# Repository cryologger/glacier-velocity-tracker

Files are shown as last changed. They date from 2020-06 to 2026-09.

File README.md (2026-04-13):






# Cryologger - Glacier Velocity Tracker (GVT)
### Note: This documentation is currently under development.
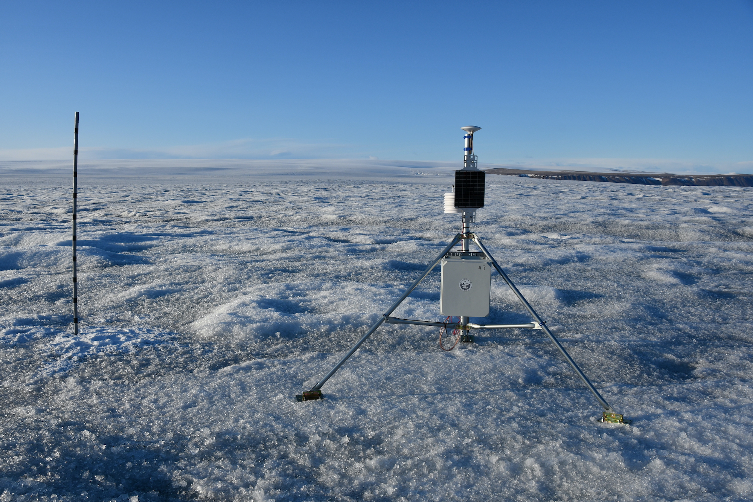
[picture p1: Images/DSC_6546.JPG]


## 1.0 Introduction

Reliance on expensive and proprietary commercial data acquisition and telemetry systems can present a barrier to monitoring remote polar environments. The development of low-cost, open-source instrumentation can greatly reduce the cost of research in remote locations, improve the spatiotemporal resolution of collected data, and provide new ways to observe and monitor the cryosphere. 

The [Cryologger Glacier Velocity Tracker (GVT)](https://github.com/cryologger/glacier-velocity-tracker) is a novel [Cryologger](https://github.com/cryologger) design configuration intended to collect high temporal resolution velocity measurements to assess glacier dynamics on daily timescales in the Canadian Arctic. The system is based on the Arduino electronics platform and harnesses the u-blox ZED-F9P multi-frequency Global Navigation Satellite System (GNSS) receiver.

## 2.0 Methods

### 2.1 Design
The Cryologger GVT is based on the open-source Arduino platform (www.arduino.cc). Code is written using the Arduino Integrated Development Environment (IDE) and benefits from the availability of community-generated libraries.

The design of the Cryologger GVT takes into consideration several key principles, including cost-effectiveness, power efficiency, modularity, ruggedness, and ease of use. It is comprised of off-the-shelf components that do not require specialized tools or training, making it accessible to researchers, citizen scientists, and hobbyists alike. These selected components are also resistant to harsh environmental conditions, ensuring year-round continuous cold-weather operation.

#### 2.1.1 Bill of materials

The Cryologger GVT is built using almost exclusively using components from [SparkFun](https://www.sparkfun.com/), with a list of the main components shown below. For a more detailed bill of materials, including requirements for power and mounting of a complete deployable system, please see [ASSEMBLY.md](/Documentation/ASSEMBLY.md).

**Table 1.** Main components making up Cryologger GVT. Prices are listed in USD and are current as of December 2023. Taxes and shipping are not included.
| Component | Product | Quantity | Cost (USD) |
| --- | --- | :---: | :---: |
| PCB | [Custom Cryologger Printed Circuit Board](https://jlcpcb.com) | 1 | $5.00 | 
| Processor | [SparkFun MicroMod Artemis Processor](https://www.sparkfun.com/products/16401) | 1 | $14.95 | 
| Carrier Board | [SparkFun MicroMod Data Logging Carrier Board](https://www.sparkfun.com/products/16829) | 1 | $21.50 | 
| GNSS Receiver | [SparkFun GPS-RTK-SMA Breakout - ZED-F9P](https://www.sparkfun.com/products/16481) | 1 | $274.95 | 
| GNSS Antenna | [SparkFun GNSS Multi-Band L1/L2 Surveying Antenna (TNC) - TOP106](https://www.sparkfun.com/products/17751) | 1 | $133.95 | 
| Display | [SparkFun Qwiic OLED Display](https://www.sparkfun.com/products/17153) | 1 | $10.95 |
| Voltage Regulator | [Pololu 5V, 600mA Step-Down Voltage Regulator D36V6F5](https://www.pololu.com/product/3792) | 1 | $6.95 |

#### 2.1.2 Design Evolution 

A carrier board was designed to simplify assembly and deployment. It provides 5.08 mm, 2-pin screw terminals for wiring the battery connection, and a resistor divider to measure battery voltage.


<p align="center"><b>Figure 1.</b> Open-source carrier board design.</p>

#### 2.1.3 Mock-up
The Cryologger GVT was originally intended to be installed in a small electronics enclosure that is mounted in a larger enclosure for deployment outdoors.


<p align="center"><b>Figure 2.</b> Open-source carrier board design.</p>

### 2.2 Operation

When initially powered on, the Cryologger GVT will attempt to establish a GNSS fix and synchronize the real-time clock (RTC) of the MicroMod Artemis Processor for up to 5 minutes. Once the RTC is synchronized, the system will set an alarm to wake at the user-specified time and then enter a low-power deep sleep.  Nominally, the system will wake daily and log data from the u-blox GNSS receiver to a microSD card for a period of 3 hours. There are three different logging modes available to the end end-user, which can be tailored to the data collection requirements and available power capacity.

Versions 2.2.1 and above of the Cryologger GVT are equipped with an OLED display. This display is used to provide detailed information to the end user about the status of the Cryologger at each stage of operation, including boot-up, initialization of components, acquisition of GNSS fix, and logging of data. 

In addition to the OLED display messages, a series of LED blink patterns can also be used to indicate system operation and guide possible troubleshooting steps that should be attempted if any errors is encountered. A detailed table of the LED blink patterns can be found in the [DEPLOYMENT.md](/Documentation/DEPLOYMET.md) documentation. 

While the system is in deep sleep, a Watchdog Timer (WDT) will wake the system to check the program has not frozen every 10 seconds and perform a reset, if necessary. This helps to ensure the long-term reliability of the system.

### 2.3 Data Processing

Data is logged in u-blox's proprietary .ubx format. Log files can be converted to RINEX using RTKLIB or Emlid Studio and submitted to NRCan's Precise Point Positioning (PPP) tool: https://webapp.geod.nrcan.gc.ca/geod/tools-outils/ppp.php

For a more detailed guide on the processing of data, please see "[PROCESSING.md](/Documentation/PROCESSING.md).

## 3.0 Deployments

Between 2021 and 2023, a total of 28 Cryologger GVT deployments were made by several different academic institutions, including the Univerity of Ottawa, Carleton University, University of Waterloo (Canada), Carnegie Mellon University (United States), and University of Fribourg (Switzerland). These deployments were made on glaciers in several geographically distinct locations, including Canada, the United States and Kyrgyzstan. Two case studies of deployments made by the University of Ottawa and the University of Waterloo on glaciers in the Yukon and Nunvaut, Canada are explored in more detail below.


<p align="left"><b>Figure 3.</b> Map of Cryologger GVT deployments made between 2021 and 2023.</p>

### 3.1 Lowell Glacier, Yukon, Canada


<p align="left"><b>Figure 4.</b> Map of Cryologger GVT deployments made in 2021 on the Lowell Glacier, Yukon.</p>

### 3.2 Belcher Glacier, Devon Island, Nunavut, Canada


<p align="left"><b>Figure 5.</b> Map of Cryologger GVT deployments made in 2021 on the Lowell Glacier, Yukon and Belcher Glacier, Devon Island, Nunavut.</p>

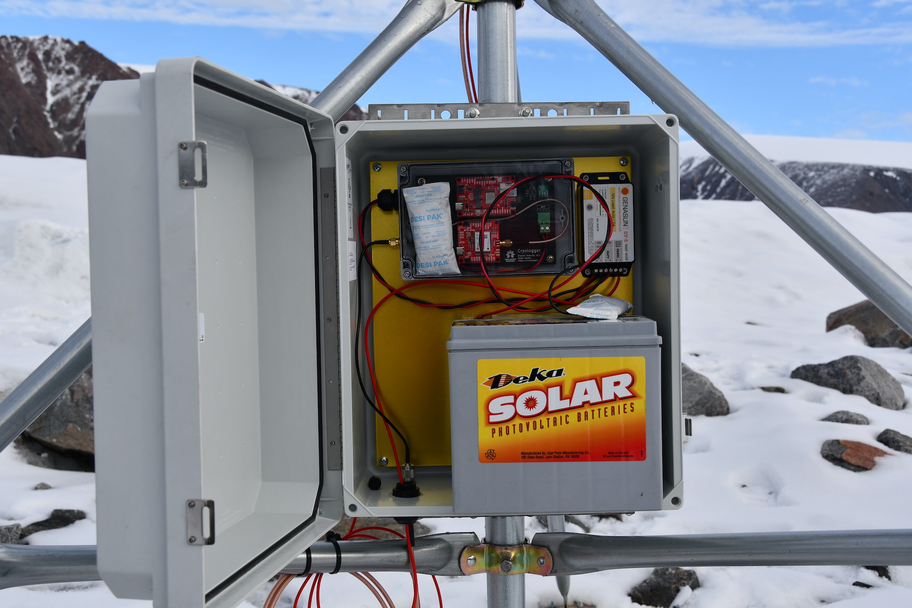
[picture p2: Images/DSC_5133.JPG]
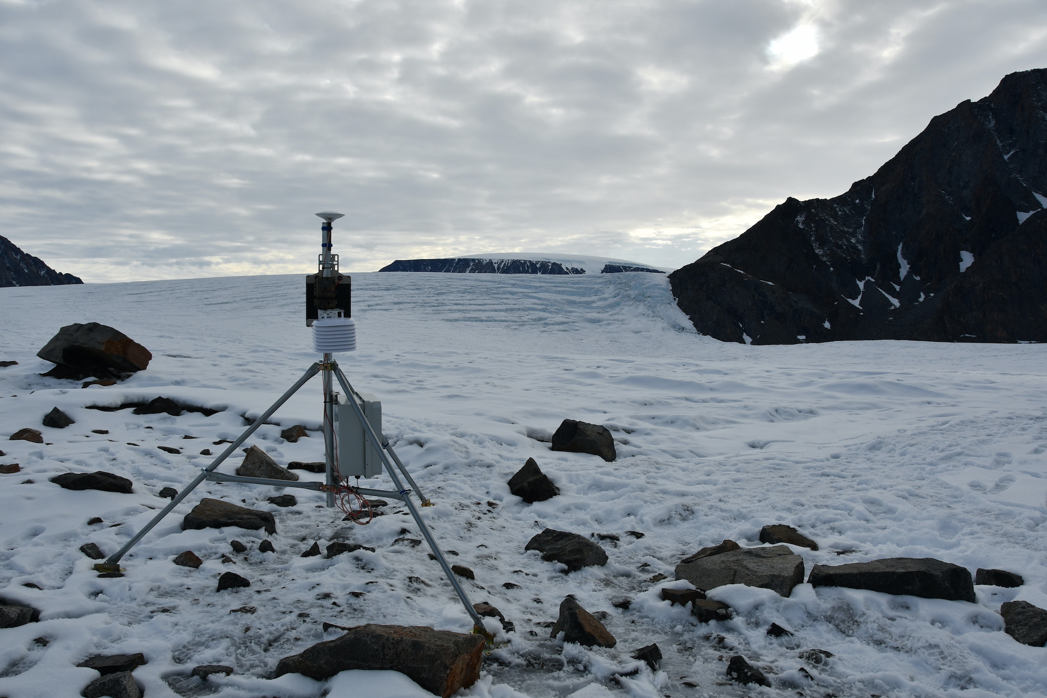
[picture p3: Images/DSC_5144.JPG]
<p align="center">&nbsp;&nbsp;</p>
<p align="left"><b>Figure 6.</b> Deployment of the "Belcher Lower" Cryologger GVT on the Belcher Glacier, Devon Island, Nunavut.</p>

## 4.0 Results

Preliminary results from the 2021 deployments of Cryologger GVTs on Lowell Glacier, Kluane National Park, Yukon and Belcher Glacier, Devon Island, Nunavut are presented below.

### 4.1 Lowell Glacier, Yukon, Canada

The initial Cryologger GVTs deployments on Lowell Glacier were both successful, achieving continuous operation throughout the year. 

Collected data that was PPP-processed revealed the GVTs deployed on Lowell Glacier were able to achieve daily position measurements with accuracies of <3 cm. Daily displacements ranged between 0.25 – 4.4 m d<sup>-1</sup> and annual cumulative distances were between 200 – 700 m y<sup>-1</sup>. Both systems showed evidence of ongoing glacier surge cycles and excitingly were also able to capture periods of marked glacier velocity corresponding to local rainfall events and enhanced basal sliding.


<p align="left"><b>Figure 7.</b> Cumulative distance and daily displacement of Lowell Glacier, Yukon recorded between between 2021 and 2022.</p>

### 4.2 Belcher Glacier, Devon Island, Nunavut, Canada

Cryologger GVT deployments made on Belcher Glacier were also able to achieve successful operation throughout the entire year. The data collected between 2021-2022 represents the first uninterrupted annual velocity record of the Belcher Glacier ever recorded.

PPP-processed data showed the GVTs deployed on Belcher Glacier were also able to achieve daily position measurements with accuracies of <3 cm. Daily displacements ranged between 0.18 – 0.45 m d<sup>-1</sup> and annual cumulative distances were between 75 – 150 m y<sup>-1</sup>. These results are also in agreement with velocities derived from synthetic-aperture radar (SAR) remote sensing data.


<p align="left"><b>Figure 8.</b> Cumulative distance and daily displacement of Belcher Glacier, Devon Island recorded between between 2021 and 2022.</p>

## 5.0 Conclusions

Cryologger GVT deployments have demonstrated they can achieve continuous year-round operation. Data processed with Precise Point Positioning techniques also reveals the systems can achieve daily position measurements with accuracies of <3 cm. These promising results demonstrate that open-source hardware and software can provide a reliable and cost-effective alternative to commercially available equipment for use in glaciological monitoring.

## Acknowledgements

This project would not have been possible without the designs, software and tutorials provided by the open-source community. A special thanks to the authors of and contributors to the [SparkFun u-blox GNSS Arduino Library](https://github.com/sparkfun/SparkFun_u-blox_GNSS_Arduino_Library).

## Repository Contents

* **/Documentation** - Assembly, deployment and troubleshooting guides, as well as information on components used and associated costs.

* **/Hardware** - KiCad PCB schematic and design files.

* **/Software** -  Arduino code and Python data analysis scripts.

## License Information
Cryologger code, firmware, and software is licensed under the GNU General Public License v3.0 (https://www.gnu.org/licenses/gpl-3.0.en.html). 

<p xmlns:cc="http://creativecommons.org/ns#" >Cryologger hardware is licensed under <a href="https://creativecommons.org/licenses/by-nc-sa/4.0/?ref=chooser-v1" target="_blank" rel="license noopener noreferrer" style="display:inline-block;">CC BY-NC-SA 4.0 </a></p>

Cheers,

**Adam Garbo**

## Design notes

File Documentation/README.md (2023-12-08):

# Cryologger Glacier Velocity Tracker (GVT) - Documentation
Several documentation files are available covering various aspects of the Cryologger Glacier Velocity Tracker assembly and operation.

**1) ASSEMBLY.md**
* Provides detailed instructions on how to assemble a Cryologger GVT system.

**2) INSTALLATION.md**
* Provides step-by-step instructions on installing the Arduino IDE and required board definitions and libraries, which are necessary for uploading code to the Cryologger GVT.

**3) INSTALLATION.md**
* Provides instructions on how to upgrade the firmware of the u-blox module used in the Cryologger GVT.

**4) SERVICING.md**
* A detailed guide related to the service and recovery of Cryologger GVT systems deployed on Belcher Glacier, Devon Island during 2021 Amundsen Expedition.

**5) PROCESSING.md**
* Related to Python scripts to automate RINEX conversion of .ubx files and to automated workflows to batch process data using NRCan's Precise Point Positioning (PPP) tool.

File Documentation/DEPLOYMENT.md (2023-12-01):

# Cryologger Glacier Velocity Tracker - Deployment

## Pre-deployment
### Logging Configuration

## Field Deployment
### OLED Display Messages

### LED Blink Patterns

In addition to the OLED display messages, a series of LED blink patterns can also be used to indicate system operation. The following table can be used to determine the status of the system, as well as any possible troubleshooting steps that should be attempted if an error is encountered. A detailed table of the LED blink patterns can be found in the [DEPLOYMENT.md](/Documentation/DEPLOYMET.md) documentation.

Additionally, while the system is in deep sleep, the Watchdog Timer (WDT) will wake the system to check the program has not frozen once every 10 seconds and an LED will blink briefly during this time. 

**Table 1.** LED blink patterns, associated description and troubleshooting guide.
| Blinks | Interval (s)  |   Pattern   | Description                     | Troubleshooting Steps                                 |
|:------:|:-------------:|:-----------:|---------------------------------|-------------------------------------------------------|
|    1   |      10       |   Single    | System is in deep sleep         | None                                                  |
|   10   |      0.1      |   Single    | Initialization complete         | None                                                  | 
|    2   |      2        |   Repeating | microSD failure                 | Reseat microSD card and reboot system                 |
|    3   |      2        |   Repeating | GNSS receiver failure           | Ensure components are firmly seated and reboot system |
|    1   |      1        |   Single    | GNSS signal acquisition         | None                                                  |
|    5   |      1        |   Single    | GNSS fix found & RTC synced     | None                                                  |
|    5   |      0.5      |   Single    | GNSS fix not found              | Ensure antenna cables are connected and reboot system |
| Random |      Random   |   Random    | Logging data to microSD card    | None                                                  |

## Troubleshooting

## Documentation

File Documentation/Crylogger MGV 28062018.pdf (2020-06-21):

Author: Adam Garbo | Last modified: June 28, 2018

Crylogger MGV

### 1.0 Introduction

The Cryologger MGV (Milne Glacier Velocity) system is intended to measure daily movement and velocity of the Milne Glacier on Ellesmere Island, Nunavut.

### 2.0 Contents

Each Cryologger MGV consists of the following components:
- Cryologger (1)
- ComNav K706 GNSS receiver board (1)
- ComNav AT330 GNSS antenna (1)
- Nanuk 945 enclosure (1)
- 10W solar panel (2)
- Genasun GV-4 MPPT charge controller (1)
- Fullriver DC105-12 sealed lead acid (SLA) battery (1)
- 45 cm TNC male antenna cable (1)
- 3 m TNC male antenna cable (1)
- TNC female bulkhead adapter (1)

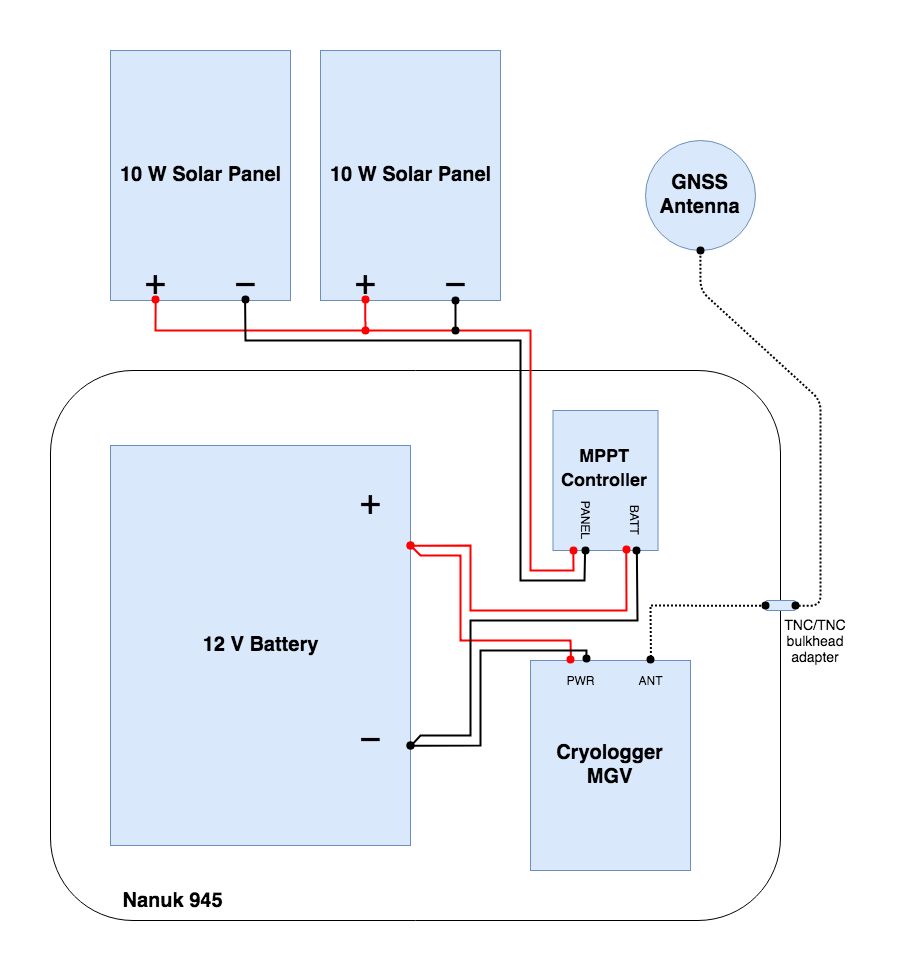
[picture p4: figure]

Figure 1. Simplified diagram of the Cryologger MGV system.

### 2.1 Cryologger MGV Components

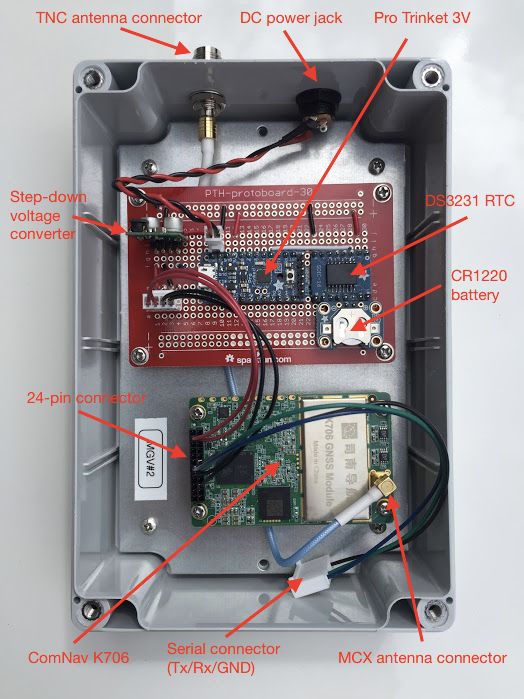
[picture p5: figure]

Figure 2. Components of the Cryologger MGV.

### 3.0 Deployment Guidelines

### 3.1 Pre-Deployment Tasks: 3.1.1 Cryologger

1) Drill holes in Nanuk 945 enclosure for 1) antenna TNC bulkhead adapter and 2) cable gland(s) for solar panel power wires.
2) Connect power wires between Fullriver DC105-12 battery and Genasun GV-4 MPPT charge controller.
3) Connect solar panel power wires in parallel and then pass through cable glands to Genasun GV-4 MPPT charge controller.
4) Apply marine silicone around enclosure holes as necessary.

### 3.1.2 Panasonic Toughbook

1) Install Arduino Software IDE (https://www.arduino.cc/en/Main/Software?)
2) Install FTDI drivers (https://learn.adafruit.com/ftdi-friend/installing-ftdi-drivers)
3) Install Adafruit Pro Trinket driver (https://learn.adafruit.com/introducing-pro-trinket/windows-setup)
4) Setup the Arduino IDE to support the Adafruit Pro Trinket board (https://learn.adafruit.com/introducing-pro-trinket/setting-up-arduino-ide)
5) Download and install the following Arduino library (https://github.com/JChristensen/DS3232RTC)
6) Install ComNav Compass Receiver Utility (CRU) software (http://www.comnavtech.com/go.asp?id=56)

### 3.2 Setup & Testing

1) Do not connect power to Cryologger until all other connections are made.
2) Connect 3 m TNC antenna cable between ComNav AT330 antenna and external TNC bulkhead adapter connection.
5) Connect 45 cm TNC antenna cable between internal TNC bulkhead adapter and Cryologger ANT-GNSS connector.
6) Connect ring terminals to battery and DC power adapter terminal block connectors.
7) Connect DC power adapter to Cryologger DC barrel jack.
8) Observe LED blink pattern.

### 3.3 Deployment

1) Follow same steps as in 3.2.

LED Descriptions
The Cryologger's onboard LED (see Figure 2.) provides information on the overall status and operation of the system. Note: Each time the Adafruit Pro Trinket 3V is reset, the bootloader will produce a default LED blinking pattern. It is following this pattern that the LED indicator should be observed. The following table defines the LED indications.

Table 2. | Cryologger LED blink patterns and descriptions.
LED Blink Pattern | Description

Observed when power turned on or reset

Quickly blinks twice (2), four
times in a row
- Bootloader blink pattern

Observed at startup (after bootloader pattern)

Quickly blinks four (4) times | - Minimum voltage threshold met.
Slowly blinks four (4) times | - Minimum voltage threshold not met.

Observed during sleep cycles every 8 seconds

Quickly blinks once (1) | - Cryologger is in sleep mode. - Minimum voltage threshold was met at last measurement. - Not recording GNSS observations.
Quickly blinks two (2) times | - Cryologger is in sleep mode. - Minimum voltage threshold was not met at last measurement. - Not recording GNSS observations.
Quickly blinks three (3) times | - Cryologger is in sleep mode. - Currently recording GNSS observations.

### 4.0 Programming the Cryologger

1) Connect the FTDI-friend to the Pro Trinket's header (shown below)
2) Open the Arduino IDE.
3) Ensure the correct board port are selected.
4) Connect the Adafruit FTDI-friend connector to the Adafruit Pro Trinket 3V header pins.
5) Upload the appropriate code to the board.

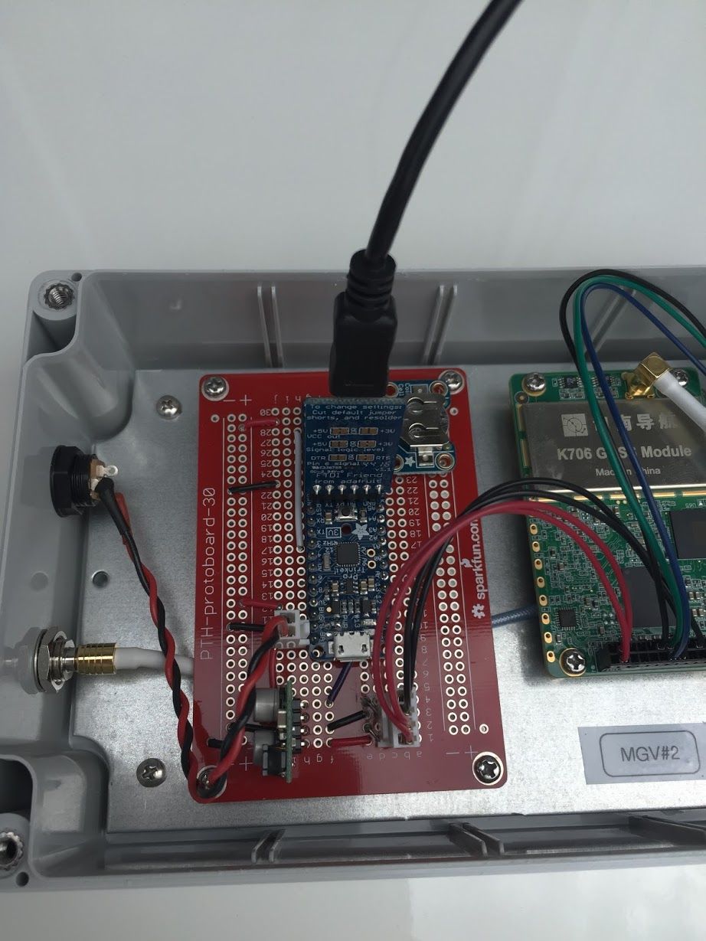
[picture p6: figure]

Figure 3. Proper orientation of Adafruit FTDI-friend connection to Pro Trinket 3V header

For additional information on how to upload code to the Arduino see:
- https://www.arduino.cc/en/main/howto
- https://learn.adafruit.com/ladyadas-learn-arduino-lesson-number-1/upload-your-first-sket ch (https://learn.adafruit.com/ladyadas-learn-arduino-lesson-number-1/upload-your-first-sketch)

### 5.0 Accessing ComNav K706 Onboard Memory (Also see: ComNav documentation)

1) Ensure proper grounding and that there are no sources of electrostatic discharge (ESD).
2) Carefully disconnect the MCX antenna cable and 24-pin header connectors from the K706 receiver board.
3) Remove the 4 PCB standoff mounting screws.
4) Remove the K706 receiver board from Cryologger and carefully insert it into the ComNav K708 dev-board.
a) The 24-pin connector should be inserted first into the dev-board, followed by the
| MCX antenna connector.
b) Be when applying pressure to the board

5) Connect DC power to the dev-board
6) Connect the USB Type B cable between the dev-board and computer
7) Turn on power to the dev-board
8) The K706's onboard memory should automatically mount as an external drive and the observation data can then be downloaded

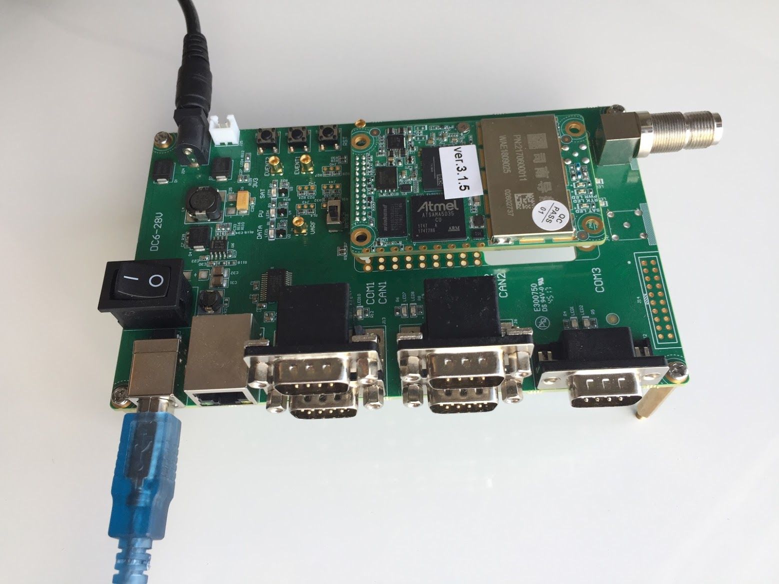
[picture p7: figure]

Figure 4. Connection for accessing K706 onboard 8 GB memory

### 6.0 ComNav Dev-Board

The image below illustrates the proper connection to make use of the K706 dev-board. It requires an antenna connection, DC power, serial cable, and serial to USB adapter. Additional information can be found in the ComNav Quick Guide V1.0.2.

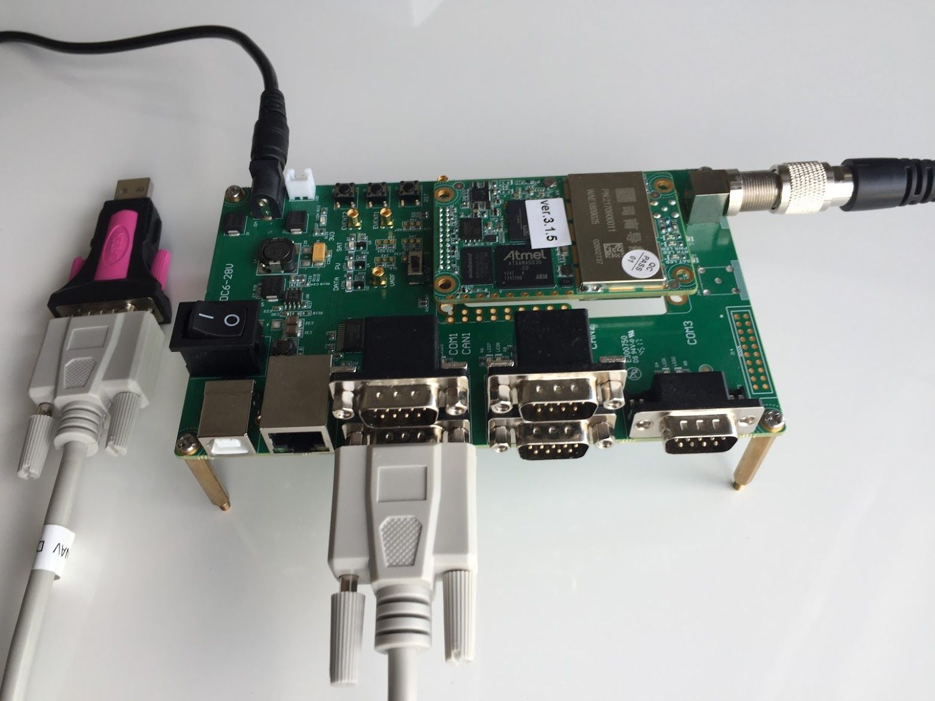
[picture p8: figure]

Figure 5. Connection required for operating the K706 with the dev-board.

### 7.0 Fieldwork Connection

It is possible to confirm the operation of the ComNav K706 receiver using the Compass Receiver Utility program and the connection displayed below.
- Connect the FTDI-friend connector with the male header pins to the white KK254 connector inside the case
- Open the CRU software
- Select the appropriate COM port and click "Connect"
- Click on the "Tracking" tab and wait for live receiver data to populate the screen

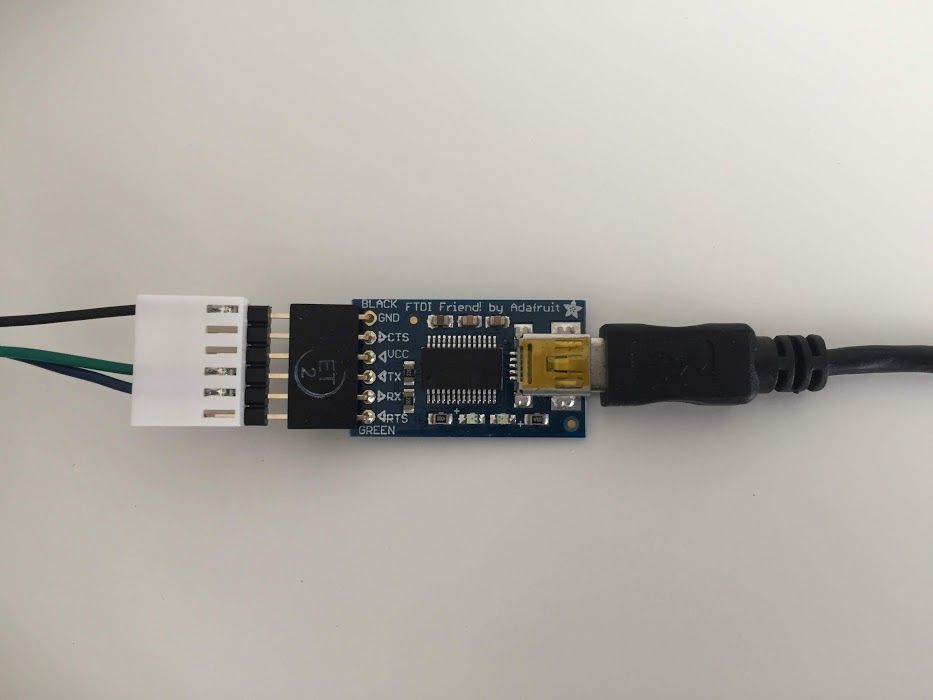
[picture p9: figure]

Figure 6. Direct Tx/Rx/GND connection to K706 board

### 8.0 Converting to RINEX

See ComNav Quick Guide V1.0.2 documentation.

### 9.0 Specifications

### 9.1 Electrical

- Voltage input ranges:
- Pro Trinket: 3-18V
- Step-down voltage regulator: 6-48V
- Quiescent draw: ~147 uA
- Active draw: ~ 250 mA

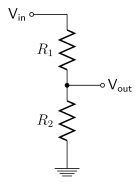
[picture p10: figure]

### 9.2 Voltage divider resistor values

- MGV #1
- R1: 10.03 MOhm
- R2: 996 kOhm
- ADC voltage divider calculation constant:
■ 996000 / (996000 + 10030000) * 1024 = ■ 92.50
- MGV #2
- R1: 10.03 MOhm
- R2: 994 kOhm
- ADC voltage divider calculation constant:

■ 994000 / (994000 + 10030000) * 1024 = ■ 92.33

### 9.3 Panel Mount Connectors

- MCX to TNC
- Diameter: 9.6 mm (0.38 inch)
- Drill bit: 3/8"
- TNC female to TNC female
- Diameter:
- Drill bit:
- DC barrel jack:
- Diameter: 12.5 mm (0.49 inch)
- Drill bit: 1/2"

Appendix A. ComNav K706 OEM Receiver Board

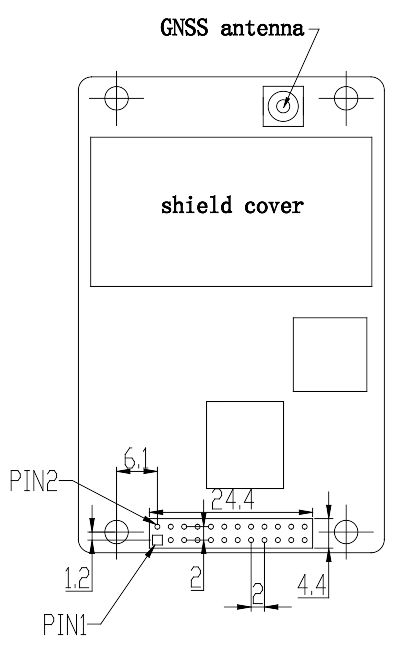
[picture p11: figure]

Figure 6. ComNav K706 top view denoting numbering of 24-pin connector.

Table x. | ComNav K706 24-pin connector. Utilized pins highlighted in colour.
2 | 4 | 6 | 8 | 10 | 12 | 14 | 16 | 18 | 20 | 22 | 24
1 | 3 | 5 | 7 | 9 | 11 | 13 | 15 | 17 | 19 | 21 | 23

Table x. Descriptions of ComNav K706 24-pin connector. Utilized pins highlighted in colour.

Pin | Signal | Type | Description
1 | SPI_CLK / ETH_RD- | MUL | multiplexed pin: SPI clock signal / ethernet receive signal (-) default: ETH_RD-
2 | SPI_CS0 / ETH_RD+ | MUL | multiplexed pin: SPI1 CS0 signal / ethernet receive signal (+) default: ETH_RD+
3 | LNA_PWR | PWR | antenna power supply
4 | 3V3 / 5V | PWR | DC power supply for board
5 | USBN | IO | USB device interface data (-)
6 | USBP / COM3_RX | MUL | multiplexed pin: USB device interface data (+) / UART received data for COM3 input default: USBP
7 | RST_SYS | I | system reset
8 | VARF / CAN1_RX | MUL | multiplexed pin: 10MHz square wave output / CAN1 input default: CAN1_RX
9 | EVENT2 / CAN1_TX | MUL | multiplexed pin: CAN2 input / RTK data LED indicator default: LED_RTK
10 | CAN2_RX / LED_RTK | MUL | multiplexed pin: CAN2 input / RTK data LED indicator default: LED_RTK
11 | EVENT1 / COM3_TX | MUL | multiplexed pin: external event input / UART transmitted data for COM3 default: EVENT1
12 | GND | PWR | ground reference
13 | COM1_TX | O | transmitted data for COM1 output
14 | COM1_RX | I | received data for COM1 input
15 | GND | PWR | ground reference
16 | COM2_TX | O | transmitted data for COM2 output
17 | COM2_RX | I | received data for COM2 input

18 | GND | PWR | ground reference
19 | PV | O | 'good solution' or valid GPS position indicator
20 | GND | PWR | ground reference
21 | PPS | O | pulse per second
22 | CAN2_TX / LED_SAT | MUL | multiplexed pin: CAN2 output / tracked satellite number indicator default: LED_SAT
23 | SPI_MISO / ETH_TD+ | MUL | multiplexed pin: SPI master in slave out signal / Ethernet transmit signal (+) default: ETH_TD+
24 | SPI_MOSI / ETH_TD- | MUL | multiplexed pin: SPI1 master out slave in signal / Ethernet transmit signal (-) default: ETH_TD-

Appendix B. | Adafruit Pro Trinket

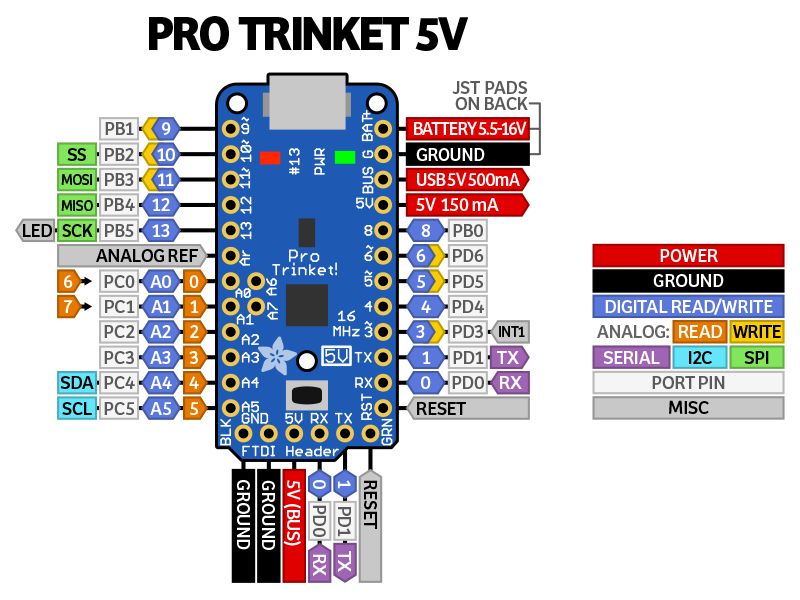
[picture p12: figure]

Figure 7. | Note that the Cryologger MGV utilizes the Adafruit Pro Trinket 3V version.

Table x. Adafruit Pro Trinket 3V pinouts and descriptions. Utilized pins highlighted in colour.
Pin | Connection | Description
Rx | Unused
Tx | Unused
D3 | RTC SQW/INT | DS3231SN SQW/INT pin external interrupt
D4 | Unused
D5 | Unused
D6 | Unused
D8 | Unused

D9 | Step-down Enable | Step-down voltage converter EN (enable) pin
D10 | Unused
D11 | Unused
D12 | Unused
D13 | LED
A0 | Voltage Divider | Battery voltage divider measurement (analog)
A1 | Unused
A2 | Unused
A3 | Unused
A4 | SDA | I2C bus (RTC)
A5 | SCL | I2C bus (RTC)
A6 | Unused
A7 | Unused
BAT | BAT | Connected to battery, voltage divider and step-down
GND | GND | Ground
BUS | Unused
3V | 3.3V | 3.3V power rail (RTC)

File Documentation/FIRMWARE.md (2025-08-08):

# u-blox ZED-F9P - Firmware Upgrade
This guide provides step-by-step instructions on how to check and upgrade the firmware of the u-blox ZED-F9P GNSS receiver used in the Cryologger glacier velocity tracker (GVT).

Update (2025-04-15): This documentation is currently outdated. Starting from version 3.x, the current firmware version is automatically displayed in the Serial Monitor output. Therefore, Step 1 is no longer necessary and can be skipped. However, Step 2 is still required to reset the u-blox module.

## Step 1: Determine firmware version
The current version of firmware on the u-blox module can be determined by uploading a new program to the Cryologger. The steps are as follows:
* Ensure the Arduino IDE v1.8.19 and SparkFun GNSS v3 library are installed (see Steps 1-4 in [INSTALLATION.md](/Documentation/INSTALLATION.md)
* In the Arduino IDE, navigate to:
  * File > Examples > SparkFun u-blox GNSS v3 > Basics > Example8_GetModuleInfo
* Upload program (see Steps 7-9 in [INSTALLATION.md](/Documentation/INSTALLATION.md))
* In the Serial Monitor output (shown below), note the value of FWVER.
  * ***Record this information in your notes for each system***
  * If the firmware version is less than 1.30, it is necessary to perform an upgrade
```
SparkFun u-blox Example
FWVER: 1.13
Firmware: HPG
PROTVER: 27.12
MOD: ZED-F9P
Unique chip ID: 0xA44C228CDD
Unique chip ID: 0xA44C228CDD
Unique chip ID: 0xA44C228CDD
```

## Step 2: Reset u-blox module
Before upgrading the firmware, it is necessary to reset the u-blox module to its factory settings.
* In the Arduino IDE, navigate to:
  * File > SparkFun u-blox GNSS v3 > Basics > Example11_ResetModule > Example1_FactoryDefaultviaI2C
* Upload the program (see Steps 7-9 in [INSTALLATION.md](/Documentation/INSTALLATION.md))
* When prompted, press a key to reset the module
```
Press a key to reset module to factory defaults
Unit has now been factory reset. Freezing...
```

## Step 3: Upgrade firmware
Upgrading of the u-blox firmware will be accomplished using the SparkFun RTK u-blox Firmware Update Tool.
* Download the SparkFun RTK u-blox Firmware Update Tool:
  * https://github.com/sparkfun/SparkFun_RTK_Firmware_Binaries/raw/main/u-blox_Update_GUI/Windows_exe/RTK_u-blox_Update_GUI.exe
* Download the most recent u-blox ZED-F9P firmware (v1.51):
  * https://content.u-blox.com/sites/default/files/2024-11/UBX_F9_100_HPG151_ZED_F9P.6c43b30ccfed539322eccedfb96ad933.bin
* Run the SparkFun RTK u-blox Firmware Update Tool
* Connect directly to u-blox ZED-F9P USB-C port 
* Confirm the COM port in use (i.e., using Device Manager)
* Click the Firmware File "Browse" button and select the downloaded binary file for the firmware update
* Select the appropriate COM port from the dropdown (click Refresh if necessary)
* Click "Update Firmware"
  * Once complete, the u-blox module will restart
* Additional documentation on how to use the SparkFun RTK u-blox Firmware Update Tool can be found on SparkFun's website:
  * https://docs.sparkfun.com/SparkFun_RTK_Firmware/firmware_update/#updating-u-blox-firmware

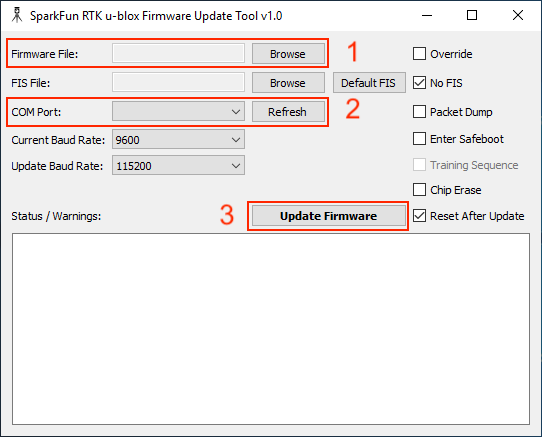
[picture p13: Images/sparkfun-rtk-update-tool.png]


## Step 4: Confirm firmware version
Once the firmware is successfully upgraded, confirm its version using the same program as in Step 1.
* In the Arduino IDE, navigate to:
  * File > Examples > SparkFun u-blox GNSS v3 > Basics > Example8_GetModuleInfo
* Upload the program
* In the output (shown below), confirm the value for FWVER has changed to v1.32
  * ***Record this information in your notes for each system***
```
SparkFun u-blox Example
FWVER: 1.32
Firmware: HPG
PROTVER: 27.30
MOD: ZED-F9P
Unique chip ID: 0xA44C228CDD
Unique chip ID: 0xA44C228CDD
Unique chip ID: 0xA44C228CDD
```
## Step 5: Upload Cryologger software
After confirming the firmware version, the latest version of Cryologger GVT software can then be reinstalled.
* See Steps 5-9 in [INSTALLATION.md](/Documentation/INSTALLATION.md)

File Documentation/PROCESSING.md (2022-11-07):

```
git clone https://github.com/rtklibexplorer/RTKLIB.git
cd RTKLIB/app/consapp/convbin/gcc
sudo make
sudo make install
```

Python script to automate RINEX conversion of .ubx files 

```                                                                                                       
import glob
from subprocess import call
from pathlib import Path

# Import CSV files from folder
input_path = "/tank/SCRATCH/agarbo/GNSS/belcher_lower/"
output_path = input_path + "RINEX"

# Create output path if required 
try:
    Path(output_path).mkdir(parents=True, exist_ok=False)
except FileExistsError:
    print("{} already exists".format(output_path))
else:
    print("{} folder was created".format(output_path))
    
# Recursively search for .ubx files
files = sorted(glob.glob(input_path + "/*.ubx", recursive=True))

# Loop through each file
for file in files:
    program = "convbin"
    arguments = "-od -os -oi -ot"
    output = "-d {}".format(output_path)
    convbin_cmd = "{} {} {} {}".format(program,arguments,output,file)
    call([convbin_cmd],shell=True)
 ```

Typical call of the convbin program:
```convbin -r ubx -od -os -oi -ot -f 2 -d /tank/SCRATCH/agarbo/GNSS/belcher_upper/RINEX /tank/SCRATCH/agarbo/GNSS/belcher_upper/20210901_160008_gvms_1.ubx```

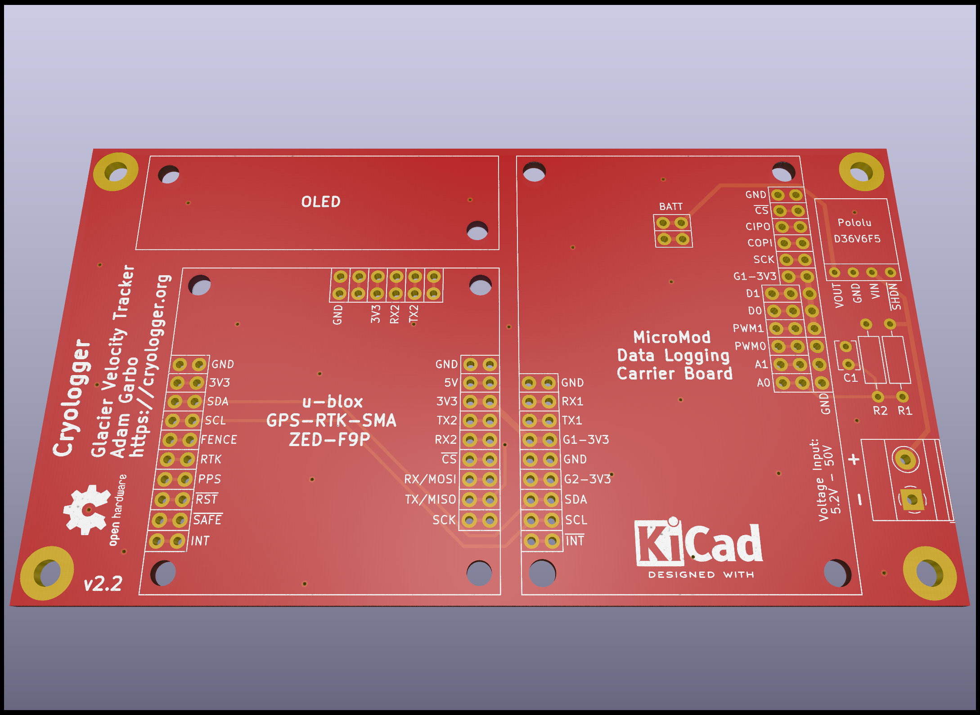
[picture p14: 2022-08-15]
Hardware/KiCad/Cryologger GVT.png

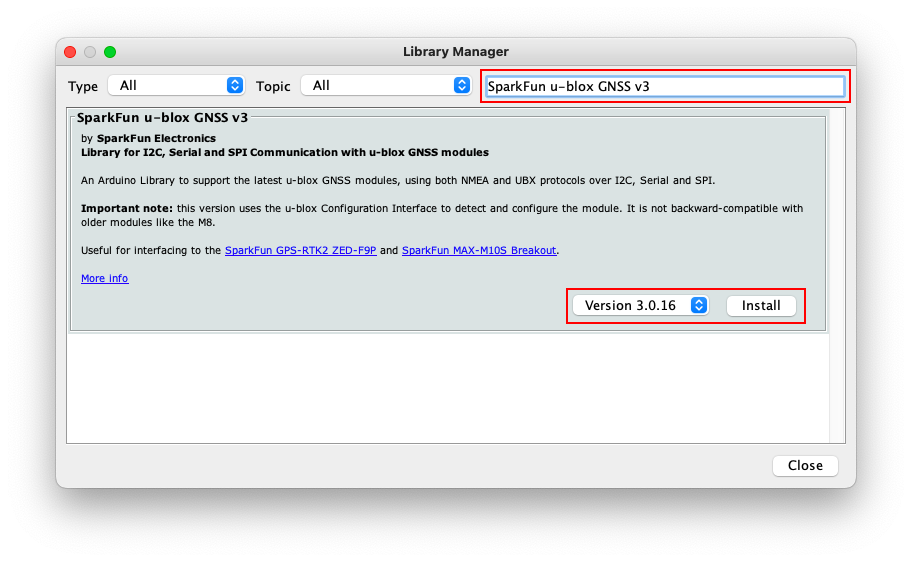
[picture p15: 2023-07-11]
Images/arduino-ide-library.png

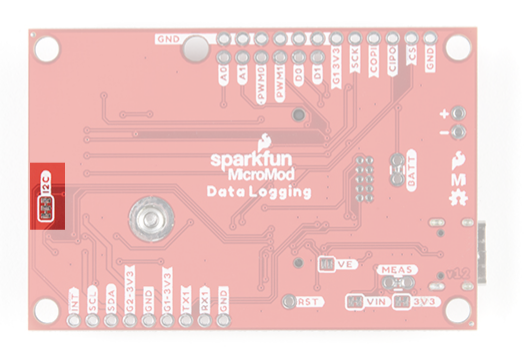
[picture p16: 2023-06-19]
Images/jumper-mmdlcb.png

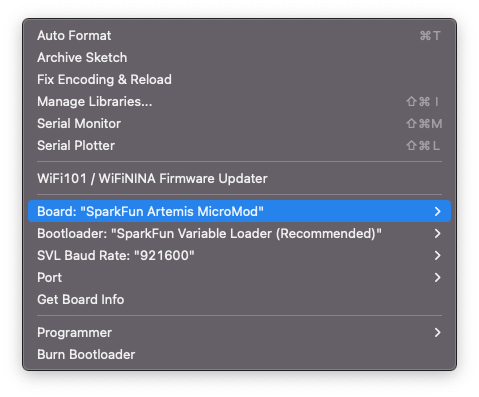
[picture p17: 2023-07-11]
Images/arduino-ide-board-1.png

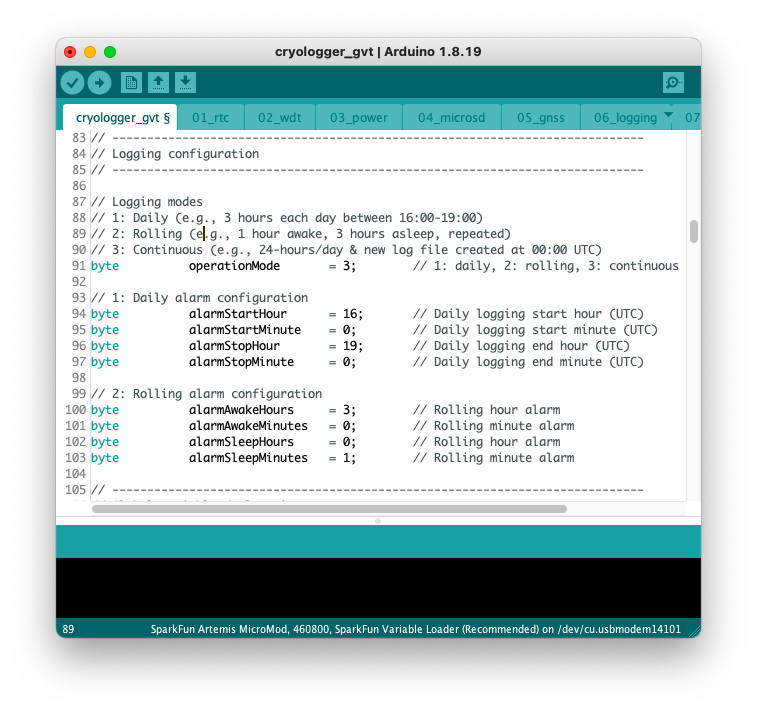
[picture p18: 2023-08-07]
Images/logging-config.png

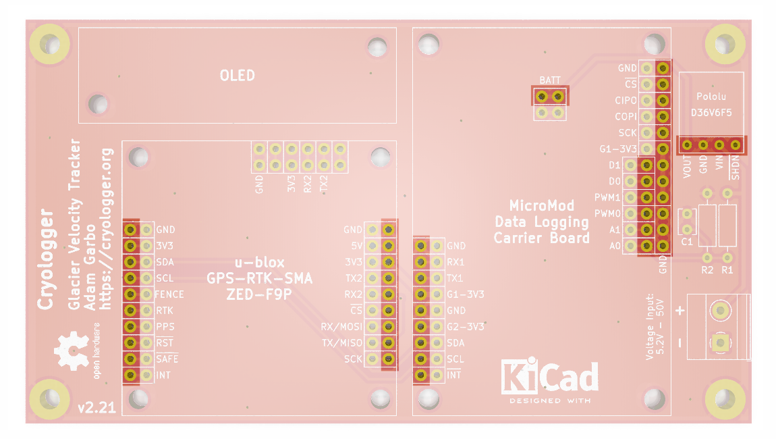
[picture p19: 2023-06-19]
Images/pcb-headers.png

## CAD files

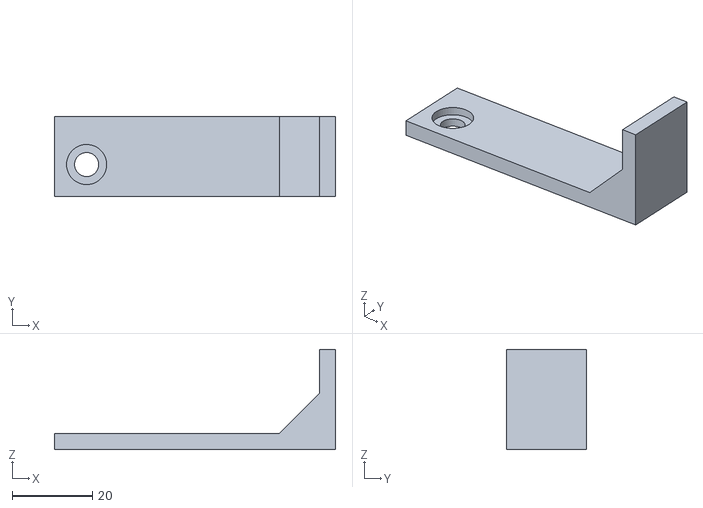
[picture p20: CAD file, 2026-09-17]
Hardware/3D Printing/battery-bracket.stl
70.0 x 20.0 x 25.0

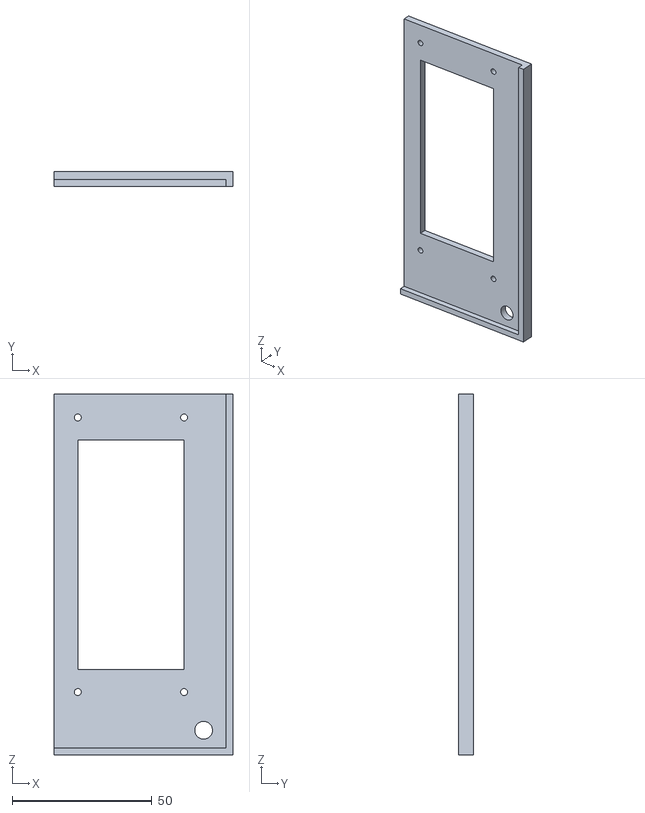
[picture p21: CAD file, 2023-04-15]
Hardware/3D Printing/genasun-drill-guide.stl
64.0 x 5.50 x 129.1

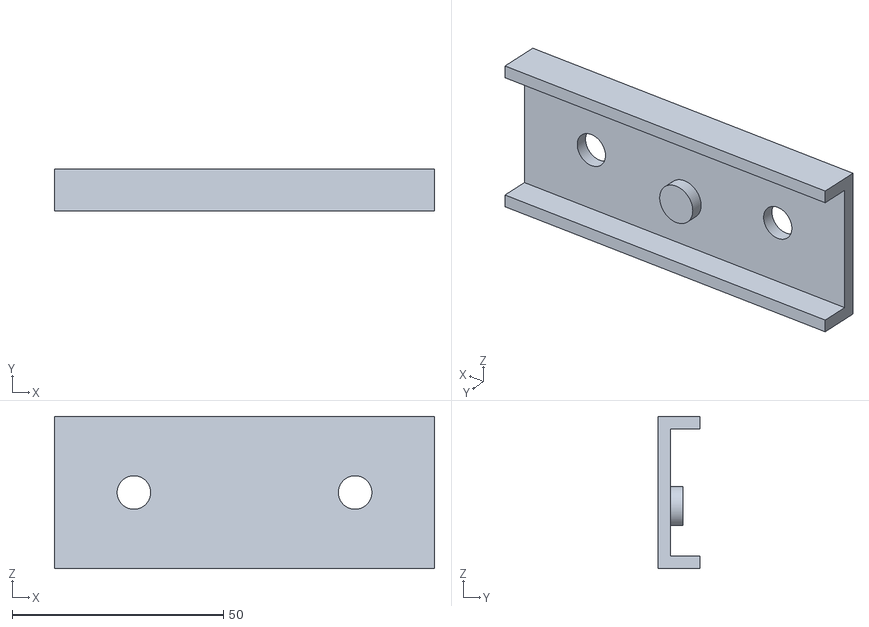
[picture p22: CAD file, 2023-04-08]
Hardware/3D Printing/solar-panel-drill-guide.stl
90.0 x 10.0 x 36.0

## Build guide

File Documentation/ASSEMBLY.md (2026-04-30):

# Cryologger Glacier Velocity Tracker - Assembly

## 1.0 Introduction
This guide provides detailed instructions on the assembly of a Cryologger GVT v2.2.1.

## 2.0 Bill of Materials
The components required to assemble a Cryologger GVT system are split into two groups: 
1) Components required for the assembly of the Cryologger (e.g., PCB, GNSS receiver, microcontroller, etc.)
2) Components required for the mounting, power and deployment of the complete system (e.g., tripod, solar panel, battery, etc.).

This guide is focused on the assembly of the Cryologger (i.e., group 1), however a bill of materials for the components pertaining to the mounting and power (i.e., group 2) is also provided.

**Table 1.** Recommended tools required for the asssembly of a Cryologger GVT v2.21.
| Tool | Recommended Product |
| --- | --- | 
| Soldering iron | [Hakko FX-888D Digital Soldering Station](https://hakkousa.com/fx-888d-digital-soldering-station.html) |
| Solder | [SparkFun Solder - 1/4lb Spool (0.020") Special Blend](https://www.sparkfun.com/products/10242) |
| Side cutter | [Hakko CHP-170 Micro Cutter](https://hakkousa.com/chp-170-micro-cutter.html) |
| Pliers | [Hakko CHP PN-2001 Pointed Nose Pliers](https://hakkousa.com/products/chp-tools/chp-hand-tools/chp-pn-2001-pointed-nose-pliers.html) |
| Hot-air rework station | [Quick 957DW+](https://www.adafruit.com/product/1869) |
| Screw driver | Phillips head screw driver |
| PCB cleaning brush | [ESD-Safe PCB Cleaning Brush](https://www.adafruit.com/product/1209) |
| PCB cleaning solution | Deionized (DI) water |

**Table 2.** Components required for asssembly of Cryologger GVT v2.21 system.
| Component | Product | Quantity | Cost (USD) |
| --- | --- | :---: | :---: | 
| PCB | [Cryologger Printed Circuit Board (PCB)](https://jlcpcb.com) | 1 |  |
| Processor | [SparkFun MicroMod Artemis Processor](https://www.sparkfun.com/products/16401) | 1 |  |
| Carrier Board | [SparkFun MicroMod Data Logging Carrier Board](https://www.sparkfun.com/products/16829) | 1 |  |
| GNSS Receiver | [SparkFun GPS-RTK-SMA Breakout - ZED-F9P](https://www.sparkfun.com/products/16481) | 1 |  |
| Display | [SparkFun Qwiic OLED Display](https://www.sparkfun.com/products/17153) | 1 |  |
| Qwiic Cable | [Qwiic Cable - 50mm](https://www.sparkfun.com/products/14426) | 1 |  |
| Voltage Regulator | [Pololu 5V, 600mA Step-Down Voltage Regulator D36V6F5](https://www.pololu.com/product/3792) | 1 |  |
| microSD Card| [SanDisk MAX Endurance 64 GB microSD](https://www.amazon.com/SanDisk-Endurance-microSDXC-Adapter-Security/dp/B084CJ96GT) | 1 |  |
| Resistor | [1 Mohms 1% MBB02070C1004FRP00](https://octopart.com/mbb02070c1004frp00-vishay-42819429?r=sp) | 1 |  |
| Resistor | [10Mohm 1% 50ppm MBB02070C1005FRP00](https://octopart.com/mbb02070c1005frp00-vishay-42881138?r=sp) | 1 |  |
| Capacitor | [0.1 uF K104K15X7RF53L2](https://octopart.com/k104k15x7rf53l2-vishay-39696446?r=sp) | 1 |  |
| Power Connector	| [PCB terminal block - MKDS 1,5/ 2-5,08 1715721](https://octopart.com/1715721-phoenix+contact-12533?r=sp) | 1 |  |
| Male Header | [SparkFun Break Away Headers - Straight](https://www.sparkfun.com/products/116) | 2 |  |
| Female Header | [Pololu 0.100" (2.54 mm) Female Header: 1x2-Pin, Straight](https://www.pololu.com/product/1012) | 1 |  |
| Female Header | [Pololu 0.100" (2.54 mm) Female Header: 1x4-Pin, Straight](https://www.pololu.com/product/1014) | 1 |  |
| Female Header | [Pololu 0.100" (2.54 mm) Female Header: 1x6-Pin, Straight](https://www.pololu.com/product/1016) | 1 |  |
| Female Header | [Pololu 0.100" (2.54 mm) Female Header: 1x9-Pin, Straight](https://www.pololu.com/product/1019) | 2 |   |
| Female Header | [Pololu 0.100" (2.54 mm) Female Header: 1x10-Pin, Straight](https://www.pololu.com/product/1020) | 1 |  |
| Female Header | [Pololu 0.100" (2.54 mm) Female Header: 1x12-Pin, Straight](https://www.pololu.com/product/1030) | 1 |  |
| Standoff | [SparkFun Standoff - Nylon (4-40; 3/4"; 10 pack)](https://www.sparkfun.com/products/11796) | 4 |  |
| Screw | [SparkFun Screw - Phillips Head (1/4", 4-40, 10 pack)](https://www.sparkfun.com/products/10453) | 8 |  |
| GNSS Antenna | [SparkFun GNSS Multi-Band L1/L2 Surveying Antenna (TNC) - TOP106](https://www.sparkfun.com/products/17751) | 1 |   |
| GNSS Antenna Cable | [SparkFun Interface Cable - SMA Female to SMA Male (25cm)](https://www.sparkfun.com/products/12861) | 1 |  |
| GNSS Antenna Cable | [SparkFun Interface Cable - SMA Male to TNC Male (300mm)](https://www.sparkfun.com/products/17833) | 1 |  |
| Enclosure | [Hammond Manufacturing 1554Q2GYCL](https://octopart.com/1554q2gycl-hammond-99088964?r=sp) | 1 |  |
| Enclosure Inner Panel | [Hammond Manufacturing 1554QPL](https://octopart.com/1554qpl-hammond-97562074?r=sp) | 1 |  |
| Power Panel Mount Connector | Bulgin<sup>1</sup> | 1 |  |
| Power Cable Connector | Bulgin<sup>1</sup> | 1 |  |
| Battery Ring Terminal | [Molex Perma-Seal Ring Terminal 14-16 AWG Wire 1/4" (M6) 19164-0026](https://octopart.com/19164-0026-molex-99569?r=sp) | 2 |  |

**Table 3.** Components making up the enclosure, mounting and power systems for Cryologger GVT version 2.0. Prices current as of April 2026. <sup>1</sup>Denotes optional component. <sup>2</sup>Denotes educational pricing.
| Component | Product | Quantity | Cost (USD) | 
| --- | --- | :---: | :---: | 
| Solar Panel | [Ameresco Solar 20 Watt Solar Panel 20J<sup>2</sup>](https://www.amerescosolar.com/20j-ameresco-solar-20-watt-solar-panel) | 1 |  $99.00 |
| Solar Panel Bracket | [Ameresco Solar HPM18-30 Solar Panel Pole Mount<sup>1,2</sup>](https://www.amerescosolar.com/hpm18-30solar-panel-pole-mount) | 1 |  $39.00 
| Solar Charge Controller | [Genasun GV-5 5A MPPT Solar Charge Controller](https://sunforgellc.com/product/gv-5/?attribute_pa_battery_voltage=12v-lead-acid&attribute_pa_battery-type=lead-acid) | 1 |  $85.00 |
| Solar Panel Power Cable | [Polarwire Arctic Ultraflex Blue Twin Trailer Cable AUF-TC162](https://store.polarwire.com/arctic-trailer-cable-16-2-gray-16ga-2-conductors/) | Variable | $0.55/ft |
| Solar Panel Cable Gland | [Heyco M4340 M20 Cable Gland](https://octopart.com/m4340-heyco-2298364?r=sp) | 2 | $5.94 |
| Battery Ring Terminal | [Molex Perma-Seal Ring Terminal 14-16 AWG Wire 1/4" (M6) 19164-0026](https://octopart.com/19164-0026-molex-99569?r=sp) | 2 | $1.00 |
| Battery | Deka SOLAR Gel 48 Ah 8G40C | 1 | ~$150.00 |
| Antenna Bulkhead Adapter | [Amphenol TNC Jk to TNC Jk 50 Ohm Str Bkhd IP67 AD-TNCJTNCJ-1](https://octopart.com/ad-tncjtncj-1-amphenol+rf-108109770?r=sp) | 1 | $53.44 |
| Antenna Cable | [GPAC GPS Antenna Cable TNC to TNC (3 m)](https://www.gpac-llc.com/product/Antenna-cables-and-cable-adapters/TNC-to-TNC-Premium-Antenna-cable) | 1 | $57.00 |
| Enclosure | [L-Com 14x12x7 Inch Weatherproof NEMA Enclosure](https://www.l-com.com/nema-enclosures-14x12x7-inch-weatherproof-nema-enclosure-only) | 1 |  $241.99 |
| Enclosure Panel | [L-Com Blank Aluminum Mounting Plate](https://www.l-com.com/nema-enclosures-blank-aluminum-mounting-plate-for-1412xx-series-enclosures) | 1 |  $56.99 |
| Pole Mount | [L-Com Enclosure Pole Mounting Kit](https://www.l-com.com/nema-enclosures-enclosure-pole-mounting-kit-pole-diameters-1-1-4-to-2-inches) | 1 | $86.99 |
| Tripod | [Onset HOBO Weather Station m 3m Tripod M-TPA](https://www.onsetcomp.com/products/mounting/m-tpa/) | 1 |  $230.00 | 
| | | **Total** | **~$1,150** |

## 3.0 Assembly

### 3.1 Cryologger PCB Assembly
**1) Collect all required components**
* It is suggested to first gather all of the components listed in the bill of materials (Table 2), required for the assembly of the Cryologger. Remove the components from their packaging and inspect them for any signs of damage.

**2) Solder through-hole resistors and capacitor**
* The first components recommended to be soldered to the Cryologger PCB are the through-hole resistors and capacitor (Figure 1). 
* Both the capacitor and resistors can be inserted into the PCB in any orientation.
* It is important to pay attention to the placement of the resistors, as they differ in resistance. 
  * R1 = 10 MOhm. Colour code: Brown Black Black Green Brown
  * R2 = 1 MOhm. Colour code: Brown Black Black Yellow Brown
* For more information on resistance colour codes, please see: https://www.digikey.com/en/resources/conversion-calculators/conversion-calculator-resistor-color-code


<p align="center"><b>Figure 1.</b> Location of through-hole resistors and capacitor to be soldered to the PCB.</p>

**3) Solder female headers to the PCB**
* A tip when soldering the female headers is to do two at a time and use a couple of uncut rows of male headers to keep them in their position. The PCB can then be turned upside down and the contacts easily soldered. 

<p align="center"><b>Figure 2.</b> Locations of female headers to be soldered to the PCB.</p>

**6) Solder screw terminal**
* Once the female headers are soldered, insert the screw terminal into the PCB, which can then be turned upside down for easy access to soldering the contacts.

<p align="center"><b>Figure 3.</b> Location of screw terminal to be soldered to the PCB.</p>

**7) Solder components**
* Insert male headers into female headers shown in Figure 2.
* Place the SparkFun MicroMod Data Logging Carrier Board and GPS-RTK2 boards onto the male header pins and solder the contacts.
* The Pololu step-down voltage regulator will also need to be soldered, but is more tricky.

**8) Clean solder flux residue**
* It is important that all solder flux residue is properly cleaned, as it can change the resistance of pins and cause issues with the normal operation of the system.
* Pour a small amount of deionized water into a clean container. 
* Dip the PCB cleaning brush into the water and then gently scrub all of the soldered connections on the bottom of the PCB and on the top components.
* If available, compressed air can be used to blow off the water.
* Otherwise, use the hot-air rework station at 300°C and with a medium sized tip to evaporate the remaining water. 
  * Do not leave the tip blowing on any one spot for longer than 3 seconds.
  * Be careful around the following locations:
    * The microSD card of the MicroMod Data Logging Carrier Board.
  
**9) Cut I2C jumpers**

See section 3.1.1 for instructions on cutting the I2C jumpers and verifying the resistance values of the system.

**10) Connect SparkFun Qwiic OLED Display**
* Attach two 3/8" nylon standoffs to the PCB with 1/4" 4-40 Phillips Head screws. 
* Connect 50 mm Qwiic cable.

**11) Upload code and test system**
* Please see https://github.com/adamgarbo/cryologger-glacier-velocity-tracker/blob/main/Documentation/INSTALLATION.md

#### 3.1.1 I2C Jumpers

When working with the Artemis Processor, I2C jumpers must be cut for all components in the system (i.e., MicroMod Data Logging Carrier Board, u-blox ZED-F9P and OLED display). The u-blox ZED-F9P is sensitive to the resistance on the I2C bus and a too high resistance can result in erratic behaviour of the system (e.g., initialization failures, intermittent logging, degraded data quality).

All I2C connections are part of the same bus, so each jumper will affect resistance of all connected components. 

For additional background information on this I2C pull-up resistor problem, see the following GitHub issue:
https://github.com/sparkfun/SparkFun_Ublox_Arduino_Library/issues/40

**1) Measure I2C bus resistance**
* Measure the resistance of following connections listed below in Table 3 before cutting the I2C jumpers. The values of the expected resistance measurements are also included.

**Table 3.** Connections to measure resistance and expected resistance values.
| Component | Connection 1| Connection 2 | Resistance (Jumpers Uncut) | Resistance (Jumpers Cut) |
| --- | :---: | :---: | :---: | :---: | 
| MicroMod Data Logging Carrier Board | G2-3V3 | SDA | ~2.2 kΩ | ~600 kΩ |
| MicroMod Data Logging Carrier Board | G2-3V3 | SCL | ~2.2 kΩ | ~600 kΩ |
| u-blox ZED-F9P | 3V3 | SDA | ~2.2 kΩ | ~250 kΩ |
| u-blox ZED-F9P | 3V3 | SCL | ~2.2 kΩ | ~250 kΩ |

**2) Cut I2C jumpers**
* Using a sharp utility knife, carefully cut each of the I2C jumpers.
* A good strategy is to make two cuts, along each of the pads so that the middle thin part of the PCB trace is removed entirely
* A digital multimeter can be used to confirm the jumper is "open" by measuring each side of the pads.

**MicroMod Data Logging Carrier Board**

mmdlcb

**GNSS**

gnss

**OLED**

oled

**3) Measure I2C bus resistance (again)**

After the I2C jumpers are cut, very high resistance values should be measured (see Table 3). Please note the resistance values may differ slightly depending on the quality of the digital multimeter (DMM) that is used. 

If the resistance measurement is lower than expected, it likely means there's still a jumper that has a connection. This can be troubleshooted by removing each component and measureing the I2C jumpers directly.

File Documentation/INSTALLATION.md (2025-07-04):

# Cryologger Glacier Velocity Tracker - Installation
This guide provides step-by-step instructions on installing the Arduino IDE and required board definitions and libraries, which are necessary for uploading code to the Cryologger GVT.

## Step 1: Download Arduino IDE  
* Navigate to https://www.arduino.cc/en/software and download the Legacy IDE (1.8.X) version of the Arduino IDE.

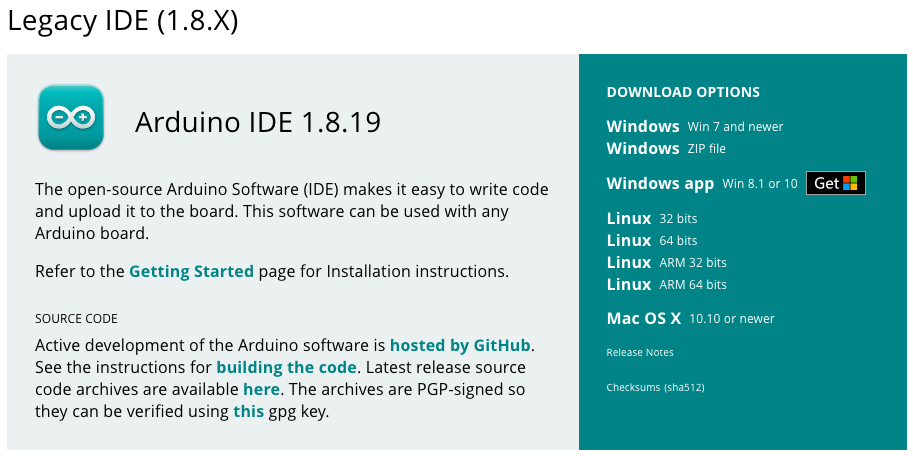
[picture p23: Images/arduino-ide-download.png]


## Step 2: Add Additional Boards Manager URL:
* In the Arduino IDE navigate to: File > Preferences
* Add the following "Additional Boards Manager URL" as shown in the screenshot below:
```https://raw.githubusercontent.com/sparkfun/Arduino_Apollo3/master/package_sparkfun_apollo3_index.json```
* Also during this step, check the "compile" and "upload" boxes for "Show verbose output during" and change "Compiler warnings" to "All"

![image](/Images/arduino-ide-preferences.png)

## Step 3: Install Board Definition
* Navigate to: Tools > Boards > Boards Manager
* Search for: SparkFun Apollo3
* Select and install version: 1.2.3
  * Warning: Do *not* install version 2.0.0 as it is incompatible with the software.
![image](/Images/arduino-ide-boards.png)

## Step 4: Install Libraries
The glacier velocity measurement system requires three external libraries. These can either be downloaded using the Arduino IDE's Library Manager (requires Internet connection), or directly from GitHub.

* Navigate to: Tools > Manage Libraries
* Search for and install the following libraries:

**Table 1.** Libraries required by Cryologger GVT. Last updated 2025-04-24.
| Library                              | Version | GitHub Repository                                               |
|--------------------------------------|:-------:|-----------------------------------------------------------------|
| SparkFun u-blox GNSS v3              |  3.1.10 | https://github.com/sparkfun/SparkFun_u-blox_GNSS_v3             |
| SdFat                                |  2.3.0  | https://github.com/greiman/SdFat                                |
| SparkFun Qwiic OLED Arduino Library  |  1.0.13 | https://github.com/sparkfun/SparkFun_Qwiic_OLED_Arduino_Library |
| ArduinoJ SON                         |  7.4.2  | https://github.com/sparkfun/SparkFun_Qwiic_OLED_Arduino_Library |

![image](/Images/arduino-ide-library.png)

## Step 5: Download Software
Code for the Cryologger GVT is made available on the following GitHub repository:
* https://github.com/adamgarbo/Cryologger_Glacier_Velocity_Tracker
* Click on "Releases" and download the v3.0.3 .zip file:

## Step 6: Connect Hardware & Configure Port Settings
* Connect the MicroMod Artemis Data Logging Carrier board via a USB-C cable.
* Install the [CH340 drivers](https://learn.sparkfun.com/tutorials/how-to-install-ch340-drivers/all#drivers-if-you-need-them), if necessary.
* In the Arduino IDE click on Tools > Board: >   
![image](/Images/arduino-ide-board-1.png)
![image](/Images/arduino-ide-board-2.png)
![image](/Images/arduino-ide-board-3.png)

* Then click on "Tools", navigate to "SVL Baud Rate" and select 460800 baud.
![image](/Images/arduino-ide-baud-1.png)
![image](/Images/arduino-ide-baud-2.png)

## Step 7: Verify Program
* Navigate to the /Software/Arduino/cryologger_gvt folder of the downloaded repository
* Double click on the `cryologger_gvt.ino` file
* Click on the checkmark in the upper left corner of the Arduino IDE program window
* Watch the output window for any compilation errors
![image](/Images/arduino-ide-verify.png)

## Step 8: Upload Program
* Once the code has compiled successfully, click on the right-pointed arrow to upload the code
* Watch the output window for compilation errors and/or success messages
* If no errors are presented, the code has been successfully uploaded.
![image](/Images/arduino-ide-upload.png)

## Step 9: Observe Serial Monitor
* After successfully uploading the program, click on the magnifying glass in the top right-hand corner to open the Serial Monitor
* Click on the baud dropdown and select 115200 baud
* Ensure the data logging mode and settings are correct
![image](/Images/arduino-ide-serial-monitor-1.png)
![image](/Images/arduino-ide-serial-monitor-2.png)

## Step 10: Next Steps
* Next to be covered is the detailed operation of the Cryologger GVT, including customized logging schedules and interpreting the OLED display messages.
* This information is made available in OPERATION.md.

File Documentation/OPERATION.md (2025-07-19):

# Operation

The Cryologger Glacier Velocity Tracker (GVT) supports flexible logging schedules to accommodate various deployment needs. As of software version 3.0 and up, users can configure the device using a JSON file placed on the microSD card, or by directly modifying the firmware.

## Logging Modes

GVT supports three primary logging modes:

| Mode        | Description |
|-------------|-------------|
| **Continuous** | Logs GNSS data continuously and creates a new file each day at 00:00 UTC. |
| **Rolling**    | Alternates between logging and sleep periods. For example, log for 30 minutes, sleep for 3 hours. |
| **Daily** *(default)* | Wakes and sleeps at fixed times each day. Ideal for conserving power during long-term deployments. |

Each mode can be tailored to match the user's operational or scientific requirements.

## Seasonal Logging Mode

Seasonal logging is an optional enhancement to the primary logging modes. When enabled, the GVT operates normally (e.g., in **daily** or **rolling** mode) for most of the year. During a defined seasonal window, it overrides the current mode and switches to **continuous** logging to collect high-frequency data.

- Implements an automated logging mode that adjusts sampling intervals based on seasonal conditions.
- Enables automated transitions across year boundaries.
- Supports both Northern and Southern Hemisphere deployments.

This feature is useful for long-term Arctic or Antarctic deployments where high-resolution data is only needed seasonally without requiring field intervention.

## Configuration Methods

GVT settings can be defined in two ways:

1. **Via JSON (`config.json`) on the SD card** – Recommended for field flexibility  
2. **Hardcoded in firmware** – Best for controlled or repeat deployments

## 1. Configuring via JSON (Recommended)

Place a file named `config.json` in the root of the microSD card. The system reads and applies these settings automatically at boot.

### Example Configuration

```json title="test.json"
{
  "uid": "GVT_25_TST",
  "operationMode": "DAILY",
  "seasonalLoggingMode": "ENABLED",
  "dailyStartHour": 17,
  "dailyStartMinute": 0,
  "dailyStopHour": 20,
  "dailyStopMinute": 0,
  "rollingAwakeHours": 1,
  "rollingAwakeMinutes": 0,
  "rollingSleepHours": 1,
  "rollingSleepMinutes": 0,
  "seasonalStartDay": 1,
  "seasonalStartMonth": 6,
  "seasonalEndDay": 30,
  "seasonalEndMonth": 9,
  "gnssMeasurementRate": 1000,
  "gnssGpsEnabled": 1,
  "gnssGloEnabled": 1,
  "gnssGalEnabled": 1,
  "gnssBdsEnabled": 0,
  "gnssSbasEnabled": 0,
  "gnssQzssEnabled": 0
}
```

### Key Parameters

| Key                   | Description |
|------------------------|-------------|
| `uid` | Unique identifier for the logger |
| `operationMode` | Logging mode: `DAILY`, `ROLLING`, or `CONTINUOUS` |
| `seasonalLoggingMode` | `ENABLED` or `DISABLED` |
| `dailyStartHour`, `dailyStartMinute` | Start of daily logging window (UTC) |
| `dailyStopHour`, `dailyStopMinute` | End of daily logging window (UTC) |
| `rollingAwakeHours`, `rollingAwakeMinutes` | Awake duration in ROLLING mode |
| `rollingSleepHours`, `rollingSleepMinutes` | Sleep duration in ROLLING mode |
| `seasonalStartDay`, `seasonalStartMonth` | Start of seasonal logging |
| `seasonalEndDay`, `seasonalEndMonth` | End of seasonal logging |
| `gnssMeasurementRate` | GNSS sampling rate (ms, 250–30000) |
| `gnssGpsEnabled`, `gnssGloEnabled`, `gnssGalEnabled`, `gnssBdsEnabled`, `gnssSbasEnabled`, `gnssQzssEnabled` | Enable (1) or disable (0) GNSS constellations |

**Tip:** Use a JSON linter to verify structure before deployment.

## 2. Hardcoded Configuration

Advanced users may opt to define settings directly in the firmware (e.g., [`main.ino`](https://github.com/cryologger/glacier-velocity-tracker/blob/76f1cdd5b8cbc1692aacf82086db6821f060ec1d/Software/Arduino/cryologger_gvt/cryologger_gvt.ino#L20-L62)). This is useful for permanent or high-stakes deployments where runtime changes are undesirable.

If using this approach, ensure that the config.json file is not present on the microSD card, as it will take precendence over the hard-code values.

```c++
// ----------------------------------------------------------------------------
// USER CONFIGURATION
// ----------------------------------------------------------------------------

// Device Identifier
char uid[20] = "GVT_25_TST";  // Default unique identifier (UID)

// Select the default operation mode (for normal periods when NOT in seasonal)
#define OPERATION_MODE DAILY  // Options: DAILY, ROLLING, CONTINUOUS

// Daily mode parameters (only used if OPERATION_MODE == DAILY)
#define DAILY_START_HOUR 17   // Logging start hour (UTC)
#define DAILY_START_MINUTE 0  // Logging start minute (UTC)
#define DAILY_STOP_HOUR 20    // Logging stop hour (UTC)
#define DAILY_STOP_MINUTE 0   // Logging stop minute (UTC)

// Rolling mode parameters (only used if OPERATION_MODE == ROLLING)
#define ROLLING_AWAKE_HOURS 1    // Awake period (hours)
#define ROLLING_AWAKE_MINUTES 0  // Awake period (minutes)
#define ROLLING_SLEEP_HOURS 1    // Sleep period (hours)
#define ROLLING_SLEEP_MINUTES 0  // Sleep period (minutes)

// Seasonal logging override
// If ENABLED and the current date is within the seasonal window,
// we switch to CONTINUOUS mode automatically.
#define SEASONAL_LOGGING_MODE ENABLED  // ENABLED or DISABLED
#define SEASONAL_START_DAY 1           // Seasonal logging start day
#define SEASONAL_START_MONTH 6         // Seasonal logging start month
#define SEASONAL_END_DAY 30            // Seasonal logging stop day
#define SEASONAL_END_MONTH 9           // Seasonal logging stop month

// GNSS Satellite Signal configuration (0=DISABLE, 1=ENABLE)
#define GNSS_MEASUREMENT_RATE 1000
#define GNSS_GPS_ENABLED 1
#define GNSS_GLO_ENABLED 1
#define GNSS_GAL_ENABLED 1
#define GNSS_BDS_ENABLED 0
#define GNSS_SBAS_ENABLED 0
#define GNSS_QZSS_ENABLED 0

// ----------------------------------------------------------------------------
//  END OF USER CONFIGURATION
// ----------------------------------------------------------------------------

```
## Best Practices

- Always test configuration changes in a controlled environment before field use.  
- Disable unused GNSS constellations to reduce power consumption.  
- Use DAILY mode with seasonal control for long-duration polar deployments.

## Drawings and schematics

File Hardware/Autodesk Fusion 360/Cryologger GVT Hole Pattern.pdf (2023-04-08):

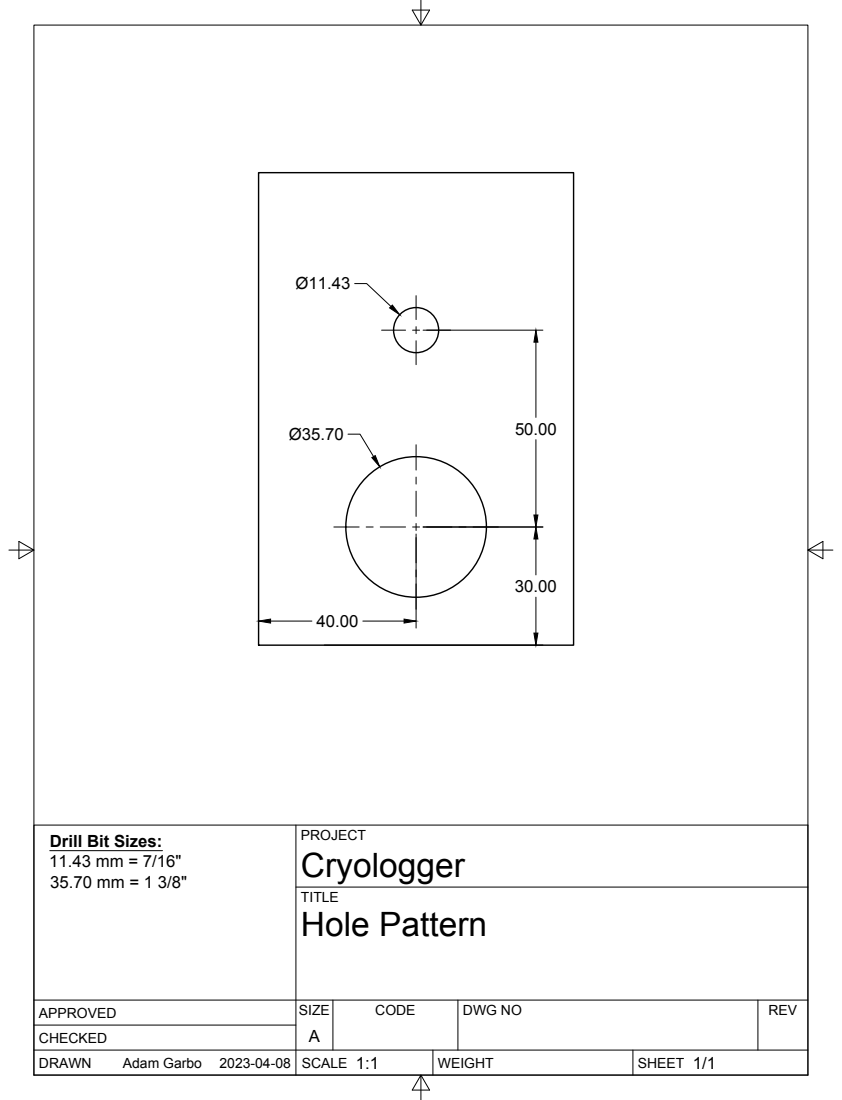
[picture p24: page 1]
SIZE; CODE; DWG NO; REV; Adam Garbo; Hole Pattern

Drill Bit Sizes:

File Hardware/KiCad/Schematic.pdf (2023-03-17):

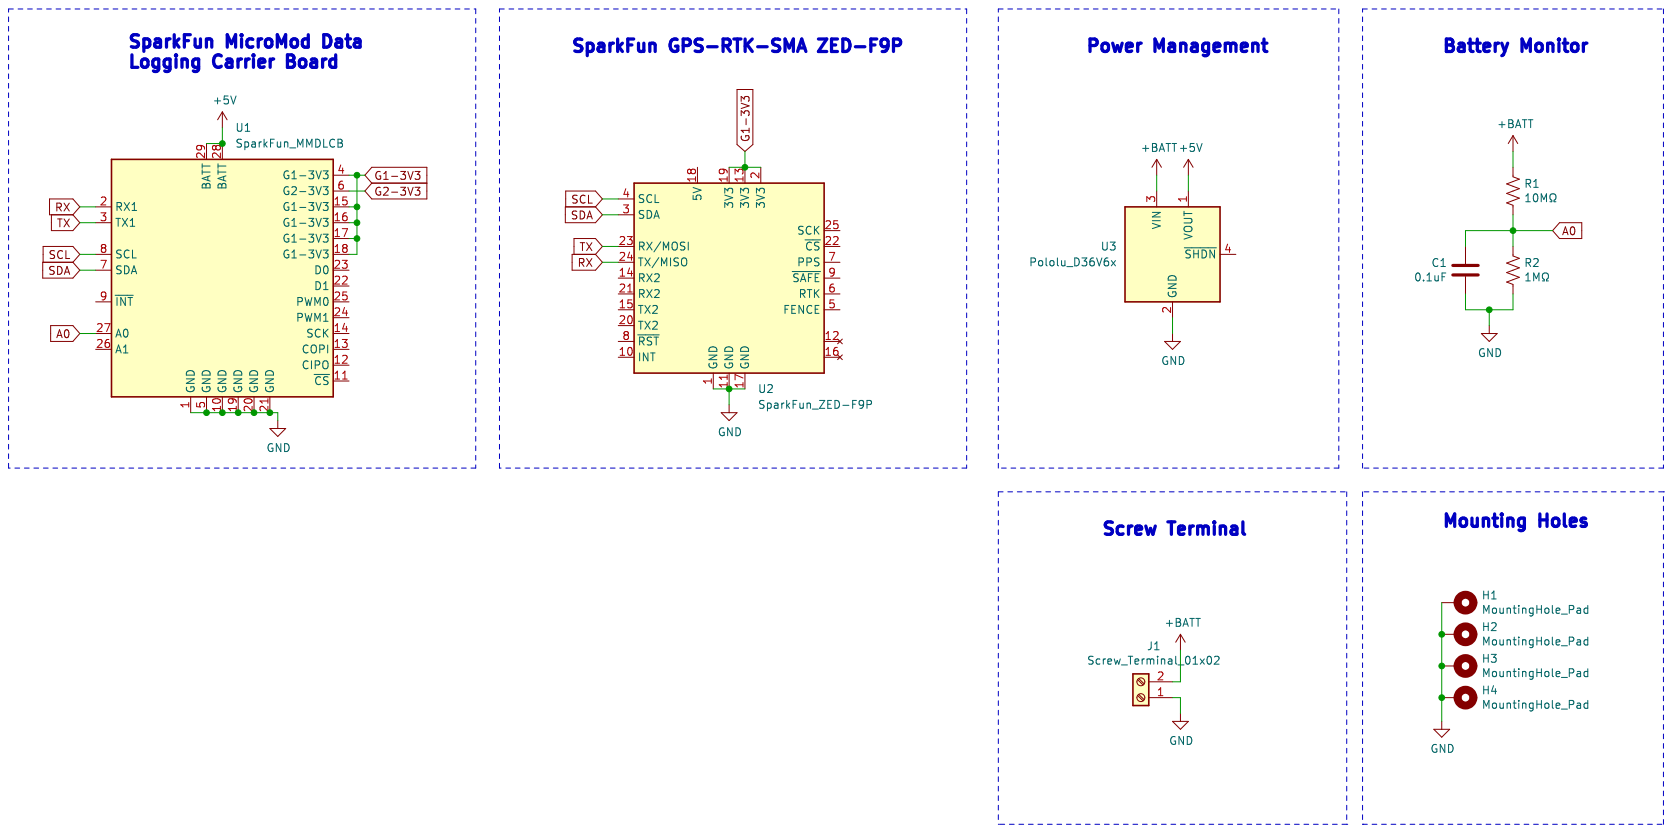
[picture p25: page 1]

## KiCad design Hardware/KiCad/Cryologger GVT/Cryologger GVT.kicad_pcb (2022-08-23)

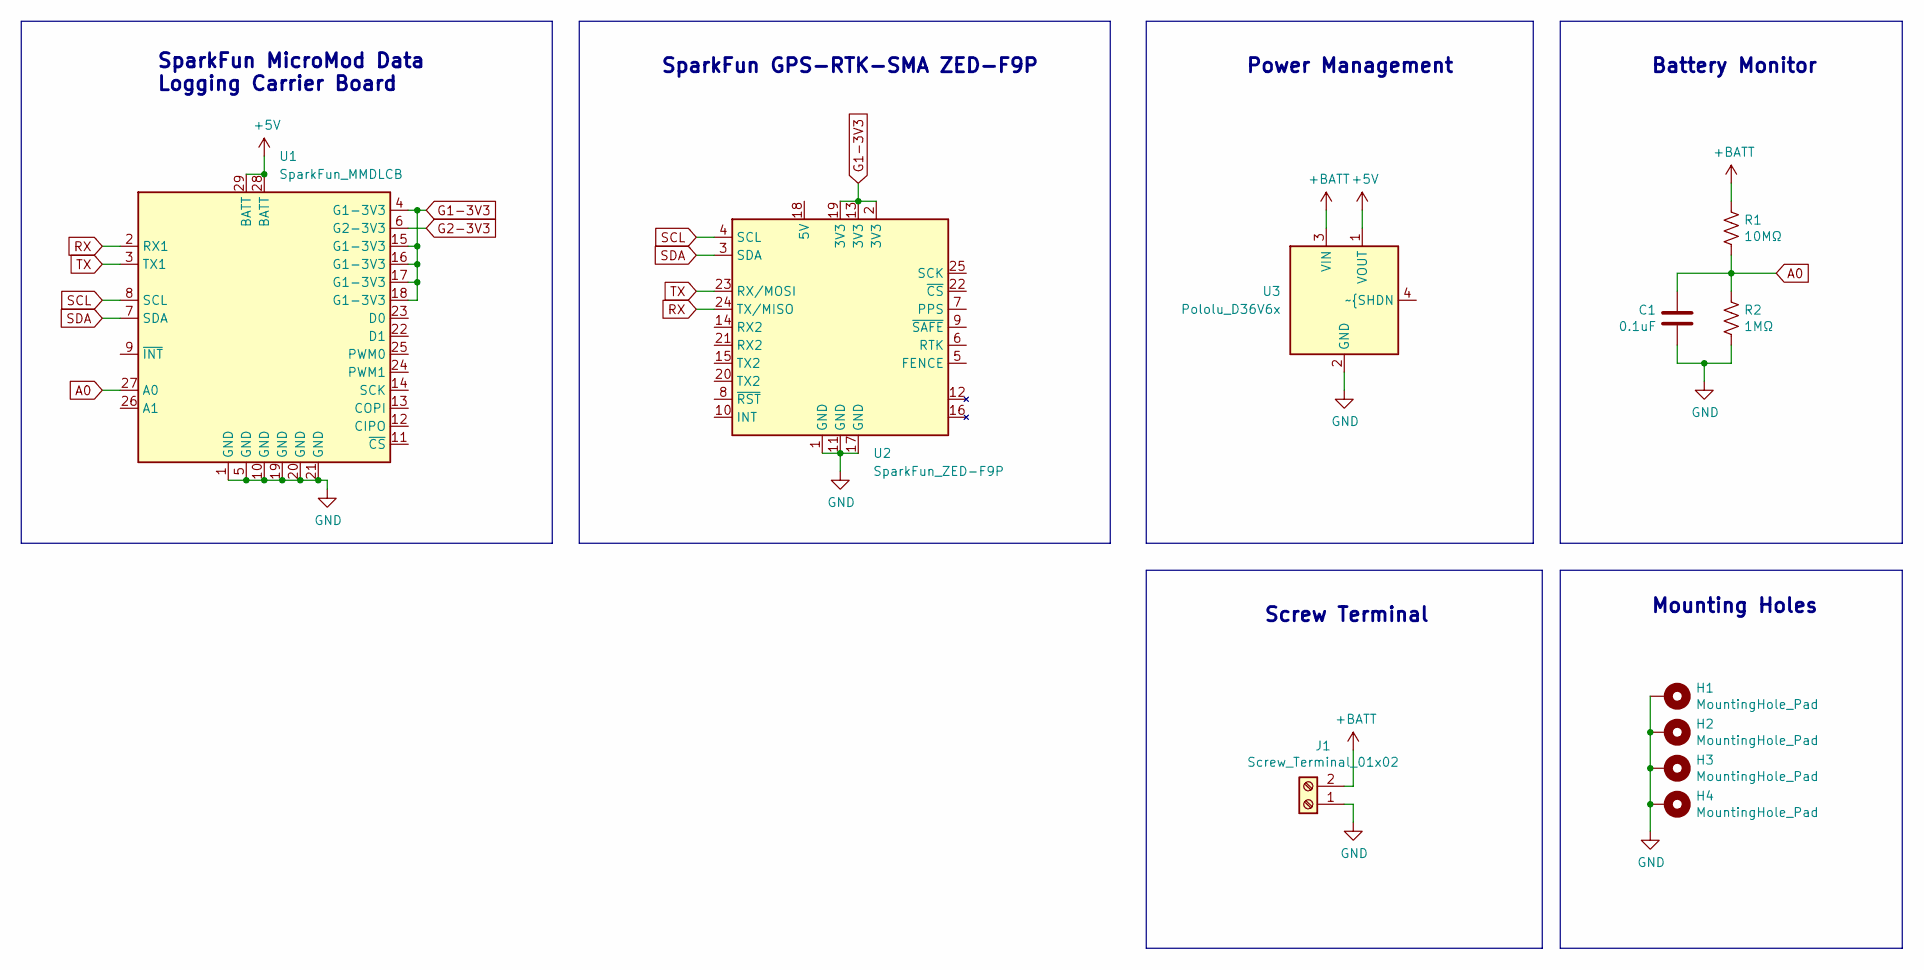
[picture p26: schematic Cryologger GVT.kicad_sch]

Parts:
C1: 0.1uF; C_Disc_D3.8mm_W2.6mm_P2.50mm
H1, H2, H3, H4: MountingHole_Pad; MountingHole_3.2mm_M3_Pad
J1: Screw_Terminal_01x02; TerminalBlock_Phoenix_MKDS-1,5-2-5.08_1x02_P5.08mm_Horizont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
R1: 10MΩ; R_Axial_DIN0207_L6.3mm_D2.5mm_P10.16mm_Horizontal
R2: 1MΩ; R_Axial_DIN0207_L6.3mm_D2.5mm_P10.16mm_Horizontal
U1: SparkFun_MMDLCB
U2: SparkFun_ZED-F9P
U3: Pololu_D36V6x; Pololu_D36V6x_Hor

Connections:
+5V: U1.28 (BATT), U1.29 (BATT), U3.1 (VOUT)
+BATT: J1.2, R1.1, U3.3 (VIN)
A0: C1.1, R1.2, R2.1, U1.27 (A0)
G1-3V3: U1.4 (G1-3V3), U1.15 (G1-3V3), U1.16 (G1-3V3), U1.17 (G1-3V3), U1.18 (G1-3V3), U2.2 (3V3), U2.13 (3V3), U2.19 (3V3)
G2-3V3: U1.6 (G2-3V3)
GND: C1.2, H1.1, H2.1, H3.1, H4.1, J1.1, R2.2, U1.1 (GND), U1.5 (GND), U1.10 (GND), U1.19 (GND), U1.20 (GND), U1.21 (GND), U2.1 (GND), U2.11 (GND), U2.17 (GND), U3.2 (GND)
RX: U1.2 (RX1), U2.24 (TX/MISO)
SCL: U1.8 (SCL), U2.4 (SCL)
SDA: U1.7 (SDA), U2.3 (SDA)
TX: U1.3 (TX1), U2.23 (RX/MOSI)

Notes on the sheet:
Battery Monitor
Screw Terminal
SparkFun MicroMod Data Logging Carrier Board
Mounting Holes
Power Management
SparkFun GPS-RTK-SMA ZED-F9P

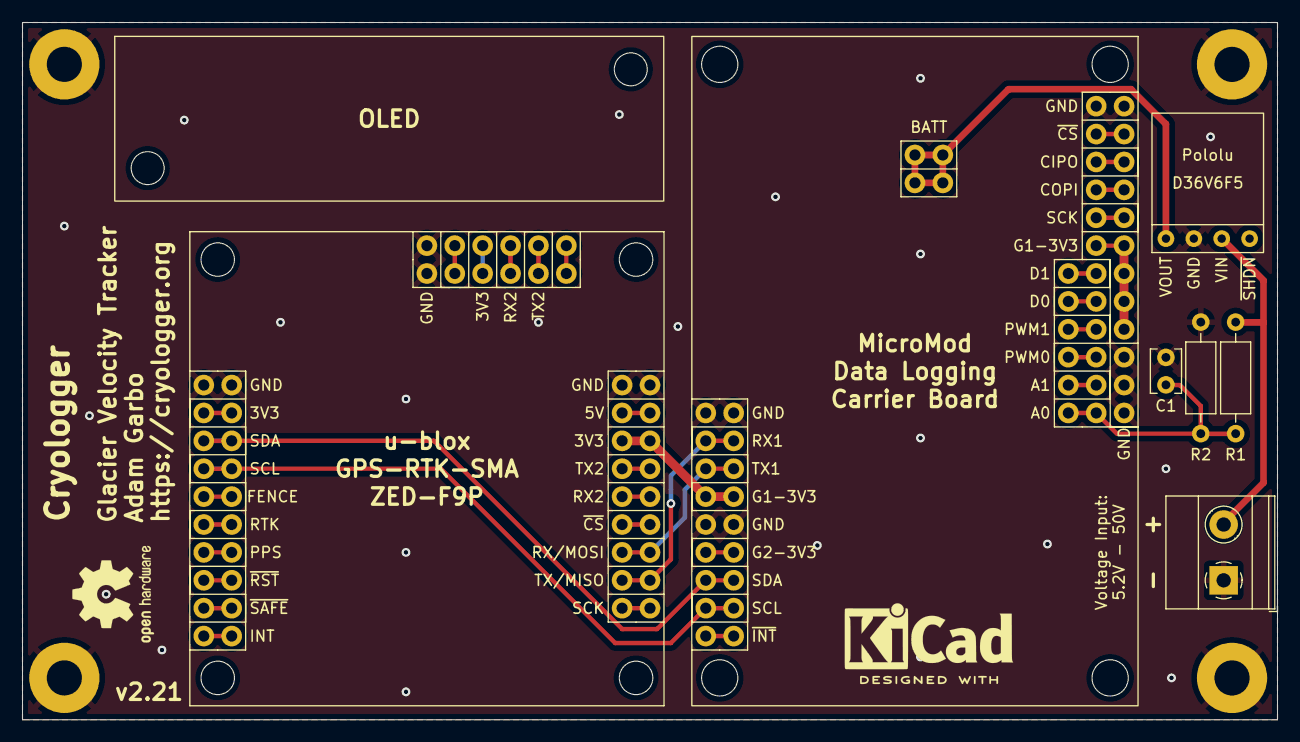
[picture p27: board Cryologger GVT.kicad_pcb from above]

Board: 2 copper layers, 114.3 x 63.5 mm, 11 parts (0 on the bottom side), 9 nets.

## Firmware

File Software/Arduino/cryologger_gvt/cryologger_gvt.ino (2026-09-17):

/*
  Title:      Cryologger - Glacier Velocity Tracker (GVT)
  Author:     Adam Garbo
  Version:    3.0.6
  Date:       September 17, 2026
  Copyright:  (C) Adam Garbo
  License:    GPLv3. See LICENSE file for more information.

  Components:
  - SparkFun Artemis Processor
  - SparkFun MicroMod Data Logging Carrier Board
  - SparkFun GPS-RTK-SMA Breakout - ZED-F9P (Qwiic)
  - SparkFun Qwiic OLED Display
  - Pololu 5V 600mA Step-Down Voltage Regulator D36V6F5

  Board Definitions:
  - SparkFun Apollo3 Boards v1.2.3

  Comments:
  - Developed for autonomous, long-term glacier velocity monitoring.
  - Tested using SparkFun Apollo3 Boards v1.2.3. Other versions may behave differently.
  - Sketch uses 131368 bytes (13%) of program storage space. Maximum is 960000 bytes.
  - Global variables use 54284 bytes of dynamic memory.
*/

// ----------------------------------------------------------------------------
// USER CONFIGURATION
// ----------------------------------------------------------------------------

// Device Identifier
char uid[20] = "GVT_26_TST";  // Default unique identifier (UID)

// Select the default operation mode (for normal periods when NOT in seasonal)
#define OPERATION_MODE DAILY  // Options: DAILY, ROLLING, CONTINUOUS

// Daily mode parameters (only used if OPERATION_MODE == DAILY)
#define DAILY_START_HOUR 17   // Logging start hour (UTC)
#define DAILY_START_MINUTE 0  // Logging start minute (UTC)
#define DAILY_STOP_HOUR 20    // Logging stop hour (UTC)
#define DAILY_STOP_MINUTE 0   // Logging stop minute (UTC)

// Rolling mode parameters (only used if OPERATION_MODE == ROLLING)
#define ROLLING_AWAKE_HOURS 1    // Awake period (hours)
#define ROLLING_AWAKE_MINUTES 0  // Awake period (minutes)
#define ROLLING_SLEEP_HOURS 1    // Sleep period (hours)
#define ROLLING_SLEEP_MINUTES 0  // Sleep period (minutes)

// Seasonal logging override
// If ENABLED and the current date is within the seasonal window,
// we switch to CONTINUOUS mode automatically.
#define SEASONAL_LOGGING_MODE DISABLED  // ENABLED or DISABLED
#define SEASONAL_START_DAY 1            // Seasonal logging start day
#define SEASONAL_START_MONTH 6          // Seasonal logging start month
#define SEASONAL_END_DAY 30             // Seasonal logging stop day
#define SEASONAL_END_MONTH 9            // Seasonal logging stop month

// GNSS Satellite Signal configuration (0=DISABLE, 1=ENABLE)
#define GNSS_MEASUREMENT_RATE 5000
#define GNSS_GPS_ENABLED 1
#define GNSS_GLO_ENABLED 1
#define GNSS_GAL_ENABLED 1
#define GNSS_BDS_ENABLED 0
#define GNSS_SBAS_ENABLED 0
#define GNSS_QZSS_ENABLED 0

// ----------------------------------------------------------------------------
//  END OF USER CONFIGURATION
// ----------------------------------------------------------------------------

// ----------------------------------------------------------------------------
// Libraries                          Version     Comments
// ----------------------------------------------------------------------------
#include <ArduinoJson.h>              // 7.4.3
#include <RTC.h>                      // 1.2      Apollo3 Core v1.2.3
#include <SdFat.h>                    // 2.3.0
#include <SparkFun_Qwiic_OLED.h>      // 1.0.15
#include <SparkFun_u-blox_GNSS_v3.h>  // 3.1.15
#include <SPI.h>                      //          Apollo3 Core v1.2.3
#include <WDT.h>                      // 0.1      Apollo3 Core v1.2.3
#include <Wire.h>                     //          Apollo3 Core v1.2.3

// ----------------------------------------------------------------------------
// Firmware & Hardware Versions
// ----------------------------------------------------------------------------
#define FIRMWARE_VERSION "3.0.6"
#define HARDWARE_VERSION "2.21"

// ----------------------------------------------------------------------------
// Debugging Macros
// ----------------------------------------------------------------------------
#define DEBUG true       // Enable Serial Monitor debug messages
#define DEBUG_GNSS true  // Enable Serial Monitor GNSS positional output
#define OLED true        // Enable OLED display messages

#if DEBUG
#define DEBUG_PRINT(x) Serial.print(x)
#define DEBUG_PRINTLN(x) Serial.println(x)
#define DEBUG_PRINT_DEC(x, y) Serial.print(x, y)
#define DEBUG_PRINTLN_DEC(x, y) Serial.println(x, y)
#define DEBUG_WRITE(x) Serial.write(x)
#define DEBUG_PRINT_HEX(x) Serial.print(x, HEX)
#define DEBUG_PRINTLN_HEX(x) Serial.println(x, HEX)
#else
#define DEBUG_PRINT(x)
#define DEBUG_PRINTLN(x)
#define DEBUG_PRINT_DEC(x, y)
#define DEBUG_PRINTLN_DEC(x, y)
#define DEBUG_WRITE(x)
#define DEBUG_PRINT_HEX(x)
#define DEBUG_PRINTLN_HEX(x)
#endif

// ----------------------------------------------------------------------------
// Pin Definitions
// ----------------------------------------------------------------------------
#define PIN_MICROSD_POWER 33  // MicroSD power control (G1)
#define PIN_QWIIC_POWER 34    // Qwiic connector power control (G2)
#define PIN_SD_CS 41          // SD card Chip Select

// ----------------------------------------------------------------------------
// Peripheral Object Instantiations
// ----------------------------------------------------------------------------
APM3_RTC rtc;          // Real-Time Clock
APM3_WDT wdt;          // Watchdog Timer
SdFs sd;               // SD card filesystem
FsFile configFile;     // Configuration file on SD
FsFile logFile;        // Log file on SD
FsFile debugFile;      // Debug log file on SD
QwiicNarrowOLED oled;  // OLED display (I2C address: 0x3C)
SFE_UBLOX_GNSS gnss;   // GNSS receiver (I2C address: 0x42)

// ---------------------------------------------------------------------------
// Operation Mode Enums
// ---------------------------------------------------------------------------
enum OperationMode : uint8_t {
  DAILY = 1,
  ROLLING = 2,
  CONTINUOUS = 3
};

enum SeasonalMode : bool {
  DISABLED = 0,
  ENABLED = 1,
};

// ---------------------------------------------------------------------------
// Global Variables for Logging Modes & Times
// ---------------------------------------------------------------------------

// The user-chosen “normal” operation mode (DAILY/ROLLING/CONTINUOUS)
OperationMode operationMode = (OperationMode)OPERATION_MODE;

// Store a copy of that mode so we can revert after seasonal
OperationMode normalOperationMode = operationMode;

// The seasonal override (ENABLED or DISABLED)
SeasonalMode seasonalLoggingMode = (SeasonalMode)SEASONAL_LOGGING_MODE;

// Daily mode times
byte alarmStartHour = DAILY_START_HOUR;
byte alarmStartMinute = DAILY_START_MINUTE;
byte alarmStopHour = DAILY_STOP_HOUR;
byte alarmStopMinute = DAILY_STOP_MINUTE;

// Rolling mode times
byte alarmAwakeHours = ROLLING_AWAKE_HOURS;
byte alarmAwakeMinutes = ROLLING_AWAKE_MINUTES;
byte alarmSleepHours = ROLLING_SLEEP_HOURS;
byte alarmSleepMinutes = ROLLING_SLEEP_MINUTES;

// Seasonal window
byte alarmSeasonalStartDay = SEASONAL_START_DAY;
byte alarmSeasonalStartMonth = SEASONAL_START_MONTH;
byte alarmSeasonalEndDay = SEASONAL_END_DAY;
byte alarmSeasonalEndMonth = SEASONAL_END_MONTH;

// ----------------------------------------------------------------------------
// GNSS Measurement Rate & Satellite Signal Enables
// ----------------------------------------------------------------------------
unsigned int gnssMeasurementRate = GNSS_MEASUREMENT_RATE;
byte gnssGpsEnabled = GNSS_GPS_ENABLED;
byte gnssGloEnabled = GNSS_GLO_ENABLED;
byte gnssGalEnabled = GNSS_GAL_ENABLED;
byte gnssBdsEnabled = GNSS_BDS_ENABLED;
byte gnssSbasEnabled = GNSS_SBAS_ENABLED;
byte gnssQzssEnabled = GNSS_QZSS_ENABLED;

// ----------------------------------------------------------------------------
// Global Variables for Logging & System State
// ----------------------------------------------------------------------------
volatile bool alarmFlag = false;  // Set by RTC alarm ISR
volatile bool wdtFlag = false;    // Set by Watchdog Timer ISR
volatile int wdtCounter = 0;      // Count of WDT interrupts
volatile int wdtCounterMax = 0;   // Maximum WDT interrupt count observed

bool firstDeploymentFlag = true;     // Forces immediate logging on first wake to confirm system operation
bool seasonalPowerInitFlag = false;  // Tracks if peripherals were restored for seasonal mode
bool gnssConfigFlag = true;          // Indicates if GNSS module needs reconfiguration
bool rtcSyncFlag = false;            // Indicates if RTC is synchronized with GNSS
bool firstTimeFlag = true;           // True during the first run

// Alarm mode settings for various states
byte alarmModeInitial = 4;  // Initial RTC alarm mode (default daily)
byte alarmModeLogging = 4;  // Alarm mode during logging
byte alarmModeSleep = 4;    // Alarm mode during sleep

// Variables to track date changes
byte dateCurrent = 0;
byte dateNew = 0;

// Buffers
char logFileName[100] = "";
char debugFileName[30] = "";
char dateTimeBuffer[30] = "";

// SD card write configuration
const int sdWriteSize = 512;       // Write block size (bytes)
const int fileBufferSize = 16384;  // Buffer size (16 KB) for UBX messages
float sdTotalMB = 0.0;
float sdFreeMB = 0.0;
float sdUsedMB = 0.0;
int sdFileCount = 0;

// Global variables to store GNSS firmware info
uint8_t gnssFirmwareVersionHigh = 0;
uint8_t gnssFirmwareVersionLow = 0;
const char* gnssFirmwareType = "";
uint8_t gnssProtocolVersionHigh = 0;
uint8_t gnssProtocolVersionLow = 0;
const char* gnssModuleName = "";
bool gnssInfoAvailable = false;  // Flag to track if retrieval was successful

// Counters and timers
unsigned long debugCounter = 0;    // Count of debug messages logged
unsigned int gnssTimeout = 300;    // GNSS acquisition timeout (default = 300 seconds)
unsigned long maxBufferBytes = 0;  // Maximum buffer size used
unsigned int reading = 0;          // Battery voltage reading (analog)
unsigned int fixCounter = 0;       // Count of GNSS fixes

unsigned long previousMillis = 0;    // For millis()-based timing
unsigned long bytesWritten = 0;      // Total bytes written to microSD
unsigned long syncFailCounter = 0;   // Count of RTC synchronization failures
unsigned long writeFailCounter = 0;  // Count of SD write failures
unsigned long closeFailCounter = 0;  // Count of SD file close failures
unsigned long logStartTime = 0;      // Logging session start time (millis)
long rtcDrift = 0;                   // RTC drift measurement

// Display
uint8_t displayScreenIndex = 0;  // OLED logging screen display counter
const uint8_t numScreens = 4;

// ----------------------------------------------------------------------------
// Structures for System Status and Timers
// ----------------------------------------------------------------------------
struct OnlineStatus {
  bool microSd = false;
  bool gnss = false;
  bool oled = false;
  bool logGnss = false;
  bool logDebug = false;
} online;

struct Timer {
  unsigned long wdt;
  unsigned long rtc;
  unsigned long microSd;
  unsigned long voltage;
  unsigned long sensors;
  unsigned long gnss;
  unsigned long syncRtc;
  unsigned long logDebug;
  unsigned long logGnss;
} timer;

// ----------------------------------------------------------------------------
// Setup
// ----------------------------------------------------------------------------
void setup() {
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

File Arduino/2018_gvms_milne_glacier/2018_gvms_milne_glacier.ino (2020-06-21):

/*

  Title:          Cryologger - Milne Glacier Velocity (MGV)
  Author:         Adam Garbo
  Last modified:  June, 2018
  Description:    Glacier velocity measurement system intended for deployment on Milne Glacier, Ellesmere Island, Nunavut, Canada.

*/

// Libraries
#include <avr/interrupt.h>    // https://www.nongnu.org/avr-libc/user-manual/group__avr__interrupts.html
#include <avr/power.h>        // https://www.nongnu.org/avr-libc/user-manual/group__avr__power.html
#include <avr/sleep.h>        // https://www.nongnu.org/avr-libc/user-manual/group__avr__sleep.html
#include <avr/wdt.h>          // https://www.nongnu.org/avr-libc/user-manual/group__avr__watchdog.html
#include <DS3232RTC.h>        // https://github.com/JChristensen/DS3232RTC

// Defined constants
#define DEBUG                     // Echo data to serial port. Comment line to prevent all Serial.print() commands
#define LED                 13    // LED activity and error indicator
#define RTC_ALARM_PIN       3     // Connect DS3231 SQW/INT pin to Pro Trinket D3 (INT1)
#define STEP_DOWN_EN_PIN    9     // Connect Pololu D24V22F5 EN pin to Pro Trinket D9

// Object instantiations
time_t          t;
tmElements_t    tm;

// User defined constants
const float   resistor1     = 10030000.0;   // Measured resistance (Ohms) of voltage divider R1 (MGV 1 & 2: 10.03 MOhm)
const float   resistor2     = 996000.0;     // Measured resistance (Ohms) of voltage divider R2 (MGV 1: 994 kOhm, MGV 2: 996 kOhm)
const byte    startTime     = 17;           // Hour of day to start recording GNSS observations (24-hour UTC)
const byte    endTime       = 18;           // Hour of day to stop recording GNSS observations (24-hour UTC)
const float   minVoltage    = 11.0;         // Minimum battery voltage required for recording of GNSS observations

// Global variable declarations
bool            flag                = 0;        // Flag for LED blink pattern
volatile bool   alarmIsrWasCalled   = false;    // DS3231 alarm interrupt service routine (ISR) flag
volatile bool   wdtIsrWasCalled     = true;     // Watchdog Timer (WDR) ISR flag
volatile bool   sleeping            = true;     // Sleep flag for WDT ISR
float           batteryVoltage      = 0.0;      // Battery voltage measured from resistor voltage divider
unsigned long   alarmTime           = 2;        // DS3231 alarm interval (for debugging purposes)

// Setup
void setup()
{
#ifdef DEBUG
  Serial.begin(57600);
#endif // DEBUG

  pinMode(STEP_DOWN_EN_PIN, OUTPUT);
  digitalWrite(STEP_DOWN_EN_PIN, LOW);

  // Configure the Watchdog Timer
  configureWatchdog();

  // DS3231 Real-time clock (RTC)
  setSyncProvider(RTC.get); // Synchronizes Time library with external RTC every five minutes
#ifdef DEBUG
  if (timeStatus() != timeSet)
    Serial.println("Unable to sync with the RTC");
  else
    Serial.println("RTC has set the system time");
#endif // DEBUG

  RTC.setAlarm(ALM1_MATCH_DATE, 0, 0, 0, 1);    // Initialize alarm 1 to known value
  RTC.setAlarm(ALM2_MATCH_DATE, 0, 0, 0, 1);    // Initialize alarm 2 to known value
  RTC.alarm(ALARM_1);                           // Clear alarm 1 interrupt flag
  RTC.alarm(ALARM_2);                           // Clear alarm 2 interrupt flag
  RTC.alarmInterrupt(ALARM_1, false);           // Disable interrupt output for alarm 1
  RTC.alarmInterrupt(ALARM_2, false);           // Disable interrupt output for alarm 2
  RTC.squareWave(SQWAVE_NONE);                  // Configure INT/SQW pin for interrupt operation by disabling default square wave output
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

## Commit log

2020-08-03 Update to version 2.0
    [Qwiic GPS-RTK-SMA - ublox ZED-F9P.brd, Qwiic GPS-RTK-SMA - ublox ZED-F9P.sch, Qwiic GPS-RTK2 - ublox ZED-F9P.brd, Qwiic GPS-RTK2 - ublox ZED-F9P.sch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]
2020-08-05 Add datasheets
    [Qwiic GPS-RTK-SMA - ublox ZED-F9P.brd, Qwiic GPS-RTK-SMA - ublox ZED-F9P.sch, Qwiic GPS-RTK2 - ublox ZED-F9P.brd, Qwiic GPS-RTK2 - ublox ZED-F9P.sch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]
2020-08-07 Wrap all Serial.print() commands with F()
2021-03-17 MicroMod prototype testing changes
2021-03-24 Modify low-power code
2021-04-01 Convert print statements to debug macros
2021-04-03 Add logging settings print function
2021-04-03 Add initialization failure reattempt code
    [Qwiic GPS-RTK-SMA - ublox ZED-F9P.brd, Qwiic GPS-RTK-SMA - ublox ZED-F9P.sch, Qwiic GPS-RTK2 - ublox ZED-F9P.brd, Qwiic GPS-RTK2 - ublox ZED-F9P.sch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]
2021-04-14 Add KiCad project files
    [Cryologger GVMS-B_Cu.gbl, Cryologger GVMS-B_Mask.gbs, Cryologger GVMS-B_Paste.gbp, Cryologger GVMS-B_SilkS.gbo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]
2021-04-28 Fix u-blox power source functionality
2021-05-25 Re-enable control over Qwiic power
2021-06-22 Update KiCad files
    [Cryologger GVMS-B_Cu.gbl, Cryologger GVMS-B_Mask.gbs, Cryologger GVMS-B_Paste.gbp, Cryologger GVMS-B_SilkS.gbo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]
2021-12-08 Rename repository files
    [Cryologger GVT.kicad_pcb, Cryologger GVT.sch, Cryologger GVT.step]
2022-03-24 Add functionality to read battery voltage
    Configure system for testing prior to deployment
2022-03-27 Add 24-hour logging mode
    Minor WDT code comment improvements. Change read voltage function to return values. Add function to get time and print to buffer.
2022-03-29 Improve OLED code
    Add explicit control over internal pull-up resistors. Incorporate new reset function allowing OLED to recover from sleep/power cycles.
2022-03-29 Upload Gerber files
    [Cryologger GVMS-B_Cu.gbl, Cryologger GVMS-B_Mask.gbs, Cryologger GVMS-B_Paste.gbp, Cryologger GVMS-B_SilkS.gbo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]
2022-03-29 Rename Gerber files
    [Cryologger GVT-B_Cu.gbl, Cryologger GVT-B_Mask.gbs, Cryologger GVT-B_Paste.gbp, Cryologger GVT-B_SilkS.gbo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]
2022-03-30 Change delays to blocking for WDT reset
    Power down Qwiic connector and microSD when forcing a WDT reset.
2022-03-31 Move disabling pull-ups to before Wire.end()
    Make battery voltage analog reading global.
2022-04-04 Adjust gain and offset
    Values based on more in-depth characterization of resistor divider cirucit.
2022-04-14 Update bill of materials
2022-06-21 Minor updates
    Improve log file naming. Rename tabs to standardized Cryologger names (i.e., logging, debug). Improve debug print statements.
2022-08-04 Minor updates
    Improved code commenting. Removal of LED blink patterns.
2022-08-15 Add PCB design revision v2.2
    Organize existing KiCad hardware and Gerber files. Create new global library symbols and footprints.
    [Cryologger GVT-B_Cu.gbl, Cryologger GVT-B_Mask.gbs, Cryologger GVT-B_Paste.gbp, Cryologger GVT-B_SilkS.gbo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]
2022-08-23 Fix orientation of PCB OLED mounting holes
    [Cryologger GVT-B_Cu.gbl, Cryologger GVT-B_Mask.gbs, Cryologger GVT-B_Paste.gbp, Cryologger GVT-B_Silkscreen.gbo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]
2022-08-23 Minor updates
    Prepare code for 2022 Lowell Glacier deployments. Create 3D PCB image.
2023-03-17 Rename folders
    Removed old KiCad files.
    [Cryologger GVT-B_Cu.gbl, Cryologger GVT-B_Mask.gbs, Cryologger GVT-B_Paste.gbp, Cryologger GVT-B_SilkS.gbo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]
2023-04-02 Migrate code to SparkFun u-blox GNSS v3 library
    Standardized debug print statements. Removed code that would cause system to enter reset loop if component failure was encountered.
2023-04-08 Add 3D-printed solar panel drill guide files
    [Solar Panel Drill Guide.stl]
2023-04-08 Add enclosure drill pattern files
2023-04-15 Add 3D-printing drill guide files
    [Genasun GV-5 Drill Guide.stl]
2023-04-29 Organize and remove old KiCad files
    [Cryologger GVT-B_Cu.gbl, Cryologger GVT-B_Mask.gbs, Cryologger GVT-B_Paste.gbp, Cryologger GVT-B_Silkscreen.gbo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]
2023-06-19 Add images for assembly documentation
2023-06-26 Update cryologger_gvt.ino
    Updated variable names to consistent style. Improved daily and rolling alarm functionality. Added a daily check to sync RTC. Avoided unnecessary reinitialization of devices when in continuous mode. I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
2023-07-11 Being updates to revert to Arduino IDE 1.8.x
2023-07-11 Continue revisions to revert to Arduino IDE v1.8.x
2025-02-17 Add seasonal logging functionality
    Improved code commenting. Changed alarms to switch case. Adopted Clang 14.0.0 formatting. Added software and hardware versions. Changed unique identifier to serial number.
2025-02-17 Improve log file write and debug print logic
    Adopted serial number for log files.
2025-02-17 Improve efficiency of debug printing
2025-02-17 Add new peripheral power restore function
2025-02-18 Refine summer mode logging
    Added debugging code to test all power-on scenarios.
2025-03-05 Remove F() from Serial print statements
    Changed sprintf() specifiers to match variable types.
2025-03-05 Revert to simplified debug logging
    Removed Serial print statement from sleep function.
2025-03-18 Remove F() from Serial print statements
2025-03-18 Use snprintf instead of sprintf to enforce bounds
    Applied Auto Format in Arduino 2.x to ensure proper formatting.
2025-03-18 Remove ArduinoJSON deprecated containsKey() calls and replace with doc["key"].is<T>()
    Changed displayInitialize() function to use const char *device.
2025-03-28 Default RTC sync GNSS measurement rate to 1 Hz
2025-04-28 Change default measurement rate to 1 Hz
2026-02-27 Update OLED display code
    Improved OLED initialization logic when the display was not physically connected but enabled in config. Added I2C device probing and improved pull-up stabilization timing.
2026-04-28 Update bill of material pricing
2026-06-27 Add functionality to track internal CPU temperature
